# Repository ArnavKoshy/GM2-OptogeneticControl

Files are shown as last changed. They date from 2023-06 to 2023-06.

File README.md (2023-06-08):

# GM2-OptogeneticControl
A repository holding information and resources about the GM2 project about optogenetic control in bioreactors for enzyme synthesis

For information about the project, what we've done and how it relates to UN Sustainable Development Goals, see [About](About/)

For information about the testing rig used to collect light intensity data around a bioreactor, see [Testing Rig](Testing%20Rig/)

For information about our light distribution model, see [Modelling](Modelling/)

For information about the final lighting rig design to light a bioreactor, see [Lighting Rig](Lighting%20Rig/)

**For Alexandre**: A list of handover documentation we've each individually contributed to is available in [Individual handover notes](Individual%20Handover%20Notes.md)

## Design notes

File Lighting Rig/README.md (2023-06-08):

# Lighting Rig Documentation

Author: Tse En Chia

## Description
---

This folder contains all the files for the design and printing of the lighting rig.

For file description and design specifications, see [CAD Files and Design Specifications](#cad-files-and-design-specifications)

## Lighting Rig Design Information
---

In the design process of the final lighting rig, a few main requirements had to be met.

1. Adequately Light

    The lighting rig should be light enough for easy transportation and set up. Users may also choose to take measurements during the synthesis process, thus the rig should be light enough to ensure ease in removing and setting it up again.

2. Low Cost

    The premise of the project was to target users in “the poorest billion”, or specifically to be deployed in Cameroon and Kenya. The cost of our design should therefore be kept as low as possible.

3. Easily Accessible

    Our partner mentioned that in previous trials, there was difficulty in accessing and installing the LED strips within the shell of the rig. Should any maintenance be required, users would also have to access the interior of the rig.

4. Easily Modifiable

    Users who wish to adopt this method of optogenetic induction would also have varying bioreactor specifications depending on their use case. Heating jackets and water jackets may be used, and users may have different volumes of bacteria and sizes of bioreactors, all of which would affect the size of the lighting rig required. The designed rig should therefore be easily customizable for users. 

## Lighting Rig Design
---

The final design of the lighting rig is as shown in the image below. This can be viewed in the assembly file.

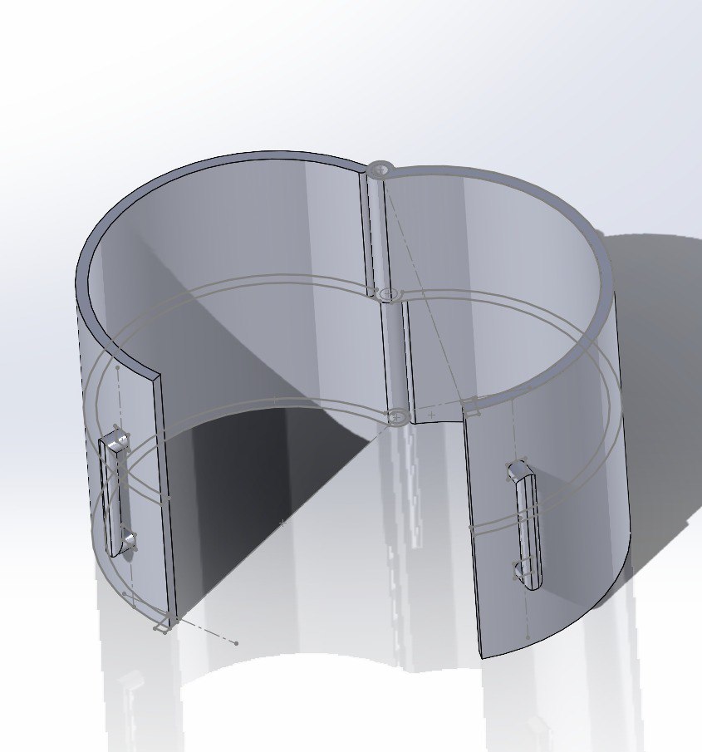
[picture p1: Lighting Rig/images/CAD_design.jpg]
CAD design


The rig uses a 6.35mm diameter rod to act as a pin for the hinge, with two halves that open to allow users to access the interior. Detailed information on the specifications can be found below in [CAD Files and Design Specifications](#cad-files-and-design-specifications).

The two halves of the rig have been designed to be secured by Velcro strips, wrapped around the handles. Users may replace this with material they deem fit to hold the halves together should a Velcro strips be unavailable (e.g. using a string to tie a knot).
  
## LED Arrangement
---

The recommended LED arrangement would be as shown in the diagram below.

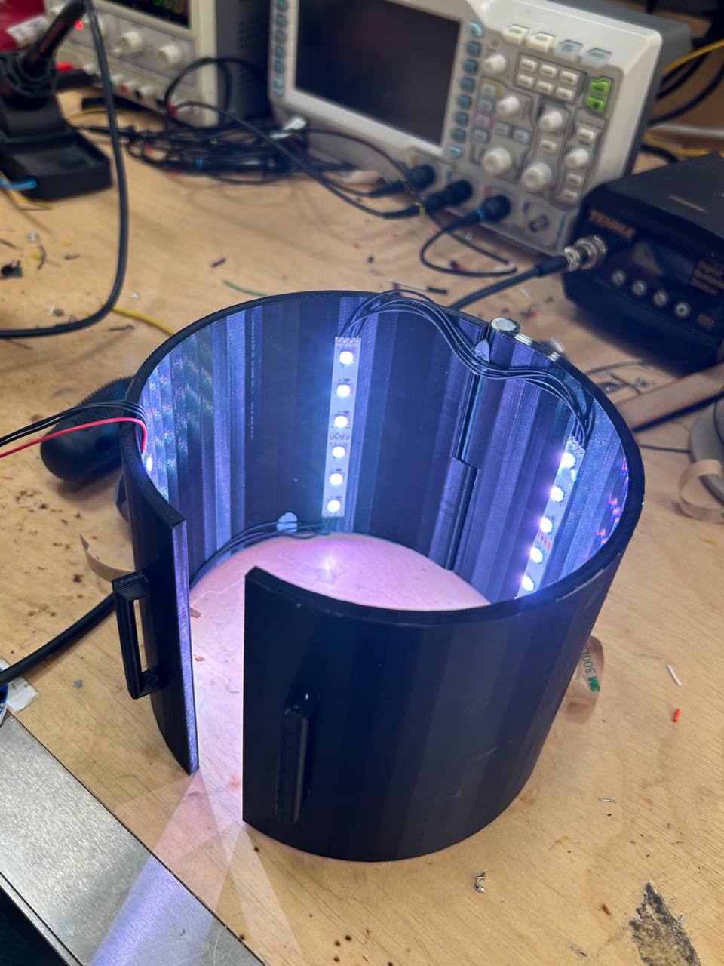
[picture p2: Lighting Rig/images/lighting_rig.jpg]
lighting rig

  
Four LED strips were installed vertically with equal spacing in the interior of the rig. The reason for this design would be because there is approximately an equal intensity of light for an arc length of about 140 degrees opposite to where the light originates from. This is supported by data collected from our tests which can be found [here](https://github.com/ArnavKoshy/GM2-OptogeneticControl/tree/main/Testing%20Rig).
  
Adding more LED strips would lead to a higher rate of bacteria synthesis but would require more electrical energy to power, which is undesirable for our target users. The recommended design saves about 80% the amount of electrical energy as compared to covering the interior with LEDs. We **do not recommend** using lesser LED strips as this would lead to some parts of the bioreactor not being illuminated.
  
It is also recommended to cover the interior of the rig with a reflective surface (e.g. aluminium foil) to maximise the intensity of light being shone into the bioreactor.

## CAD Files and Design Specifications
---

  The CAD files are as follows:

- `hinge_tube_right.SLDPRT`

  The half of the rig that contains the lower knuckle (or “hinge joint”) of the hinge. The bottom of the knuckle is sealed to prevent the rod from falling out.

- `hinge_tube_left.SLDPRT`

  The half of the rig that contains the upper knuckle of the hinge. The hole of the knuckle goes all the way through for the rod to be inserted. To further secure the rod, blutack can be used to seal the top, although not necessary.

- `prototype.SLDASM`

  Contains the assembly of the lighting rig. Can be used to view the full model.

For ease of modifying the size of the structure, both files have the following global variables. Changing the values of the variables will easily change the dimensions of the structure.
  
- `DIAMETER`

  Inner diameter of the structure. Remember to cater for the height of the LEDs to be installed, and any other equipment to be placed between the jar and the rig (e.g. water jackets). The diameter set in the design file is 142mm given a bioreactor diameter of approximately 125.5mm.

- `ROD_DIAMETER`

  Diameter of the rod used as the hinge pin. Set a buffer of 0.5mm-1mm depending on the print accuracy. The ROD_DIAMETER in the design file was set to 7mm, given that a steel rod with a diameter of 6.35mm was used.

- `HEIGHT`

  Desired height of the structure. The height in the design file was set to 130mm.

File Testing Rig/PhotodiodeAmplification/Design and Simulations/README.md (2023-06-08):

# Simulation and circuit design

This document outlines the initial design process for the amplification circuit elements, in case a ground-up redesign is considered.

## Amplifier Stage Design

###### Overview
The amplification circuit uses trans-impedance amplifiers (TIAs) to amplify the minute photodiode currents caused due to incident light. For the photodiode chosen, this current varies from $10nA$ to $50\mu A$.

The gain of the TIA is set by a single gain resistor. The output voltage is given by $I_d R_g + V_{off}$ where $I_d$ is the current through the diode, $R_g$ is the gain resistance and $V_{off}$ is the offset voltage applied to the non-inverting input. An additional capacitor is included to reduce noise.

The value of $R_g$ was chosen to allow the full range of currents through the diode to be measured. (See [Improvements](#improvements-for-redesign))

The choice to multiplex photodiodes before the amplifiers was made due to the significant cost and complexity benefits it provides. Only 3 amplifiers were needed, which amounted to a single chip, as opposed to the potential 6 ICs that would be needed without multiplexing.

###### Inclusion of Offset voltage
The amplifiers used are advertised as rail-to-rail, but actually can only drive outputs $25mV$ above $V_{ss}$ or below $V_{dd}$. 

In order to stay out of this region, a $50mV$ offset voltage was applied, so that the lowest output voltage of the TIA would always be $50mV$

###### Effect of multiplexer on resistance

When using a multiplexer before the inverting input of the amplifier, the resistance of the multiplexer was considered to confirm it had no impact on amplified reading. This was clear from a back-of-the-envelope circuit analysis, and was further verified in simulation.

## Simulation

[PhotodiodeStage.asc](PhotodiodeStage.asc) is an [LTSpice](https://www.analog.com/en/design-center/design-tools-and-calculators/ltspice-simulator.html) simulation of a single amplifier and photodiode. 

Photodiodes are not a standard part in the LTSpice library, so a phototransistor was used. This has a very similar working principle so was considered to be a usable substitute. 

The multiplexer resistance was taken into account with R3 - a $100 \Omega$ series resistance between the phototransistor and the inverting input of the amplifier.

A transient simulation has been set up for steadily increasing incident light on the phototransistor.

## Improvements for redesign

The photodiodes and amplifiers worked well in broad daylight, but were not sensitive enough for the low light intensities of bioreactor illumination. A different choice of photodiode would be beneficial, with a steeper current-light relationship. 

The gain resistance could also be changed to achieve the same effect.

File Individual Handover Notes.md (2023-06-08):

### Here's the links of handover notes that each of our group member wrote/contributed:

Arnav:
- [Modelling Handover](/Modelling/DiffuseSim/README.md)
- [Data Collection Handover](/Testing%20Rig/DataCollection/README.md)
- [Circuit Design and Simulation Notes](/Testing%20Rig/PhotodiodeAmplification/Design%20and%20Simulations/README.md)
- [Arduino Handover](Testing%20Rig/Arduino/datalogging/README.md)

Alban: 
- [Data Analysis](/Testing%20Rig/Data%20Analysis/README.md)
- [Further Testing](/Testing%20Rig/Further%20Testing/README.md)

Jasmine:  
- [Circuit Design Handover](https://github.com/ArnavKoshy/GM2-OptogeneticControl/blob/main/Testing%20Rig/PhotodiodeAmplification/Circuit%20Documentation.md)  
- [Experimental Data Analysis Handover](https://github.com/ArnavKoshy/GM2-OptogeneticControl/blob/main/Testing%20Rig/Data%20Analysis/Data%20Analysis%20Documentation.md)  

Tse En:  
- [Testing Rig Physical Design Handover](https://github.com/ArnavKoshy/GM2-OptogeneticControl/blob/main/Testing%20Rig/Physical%20Rig/README.md)
- [Lighting Rig Handover](https://github.com/ArnavKoshy/GM2-OptogeneticControl/blob/main/Lighting%20Rig/README.md)

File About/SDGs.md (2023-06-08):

# The project and Sustainable Development Goals

The project's impact can be assessed by considering how closely it aligns with the following UN [Sustainable Development Goals](https://www.globalgoals.org/goals/)

## Reduced inequalities
---
Enzymes are a crucial component when it comes to essential chemical processes such as water purification, or disease treatment and detection.
The components act as catalysts in chemical reactions, and are needed in the Global South.

The problem however, is that enzyme imports are very scarce, expensive and the delivery time is high. 
Furthermore, the local synthesis of enzymes requires reagents, which are also hard and expensive to deliver to poor countries.

Enzymes are needed in the Global South, but can't be acquired sustainably to satisfy the needs.

One solution that may be able to improve that problem is using Optogenetics.
The principle is the following: by directing light at bacteria, there is a production of enzyme. This is of course wavelength and intensity dependant, but this solution is fairly simple to implement and promising.

This allows better access to enzymes in the Global South, reducing access inequalities to products necessary for research towards other development goals.

## Resilient infrastructure - distributed production of enzymes
---
Optogenetics is conducted in a structure that is called a bioreactor. The bioreactor is container ranging in volume from 500mL to a few dozens of litres.
Once the bioreactor is acquired, and the lighting rig is setup, all there is to do is to put bacteria in the reactor and start the optogenetics process. 

Bacteria are easily accessible even in Global South countries, which enables them to have a resiliant enzyme supply chain. Moving the production of enzymes to the place of use is beneficial in improving the resilience of supply chains to disruption and shortage, as well as reducing acquisition times.

In terms of setup, the solution we came up with only uses an Arduino card, which can be run by any basic laptop, and LEDs which are easily found anywhere in the world. One step further from our project would be to design specifications that can take into account most LED specs and adapt the solution accordingly.

## Sustainable economic growth
---
Optogenetics allow countries in the Global South to not rely on enzyme or reagents import, and to produce enzymes locally. This allows independent economic growth of research sectors of these countries, without depending on foreign imports. 

Furthermore, the vast majority of the components needed to run our setup can be sourced locally.

An Arduino card, LED strips, 3D printed parts and any laptop are components that can be obtained very quickly and easily.

This makes the enzyme production local and virtually independant from any imports.

## Partnership towards the goals.
---

Enabling production of necessary enzymes in developing countries facilitates them to independently work towards other UN Sustainable Development Goals without relying on foreign supplies. 
This, coupled with the reduced acquisition time for necessary enzymes, dramatically accelerates the pace of research and progress in developing countries.

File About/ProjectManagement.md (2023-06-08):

# Project Management

## Gantt chart
To organise the project, [ClickUp](https://clickup.com/) - a project management tool - was used. This had several advantages. Tasks could be assigned to individual people. The progress of the project could be monitored centrally, and deadlines and dependencies were clear.

The Gantt chart provided a lot of value, not only to schedule tasks and monitor project progress, but also to organise dependencies and consider tasks that were blocking others.

The images below show a comparison of the initial Gantt chart plan, with the final actual chart being shown below.

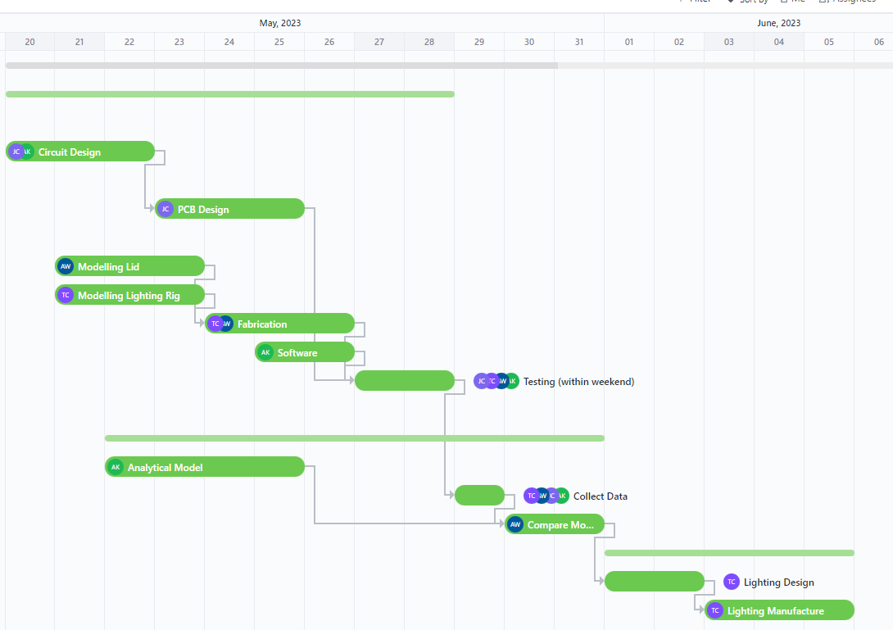
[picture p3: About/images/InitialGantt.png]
Initial chart


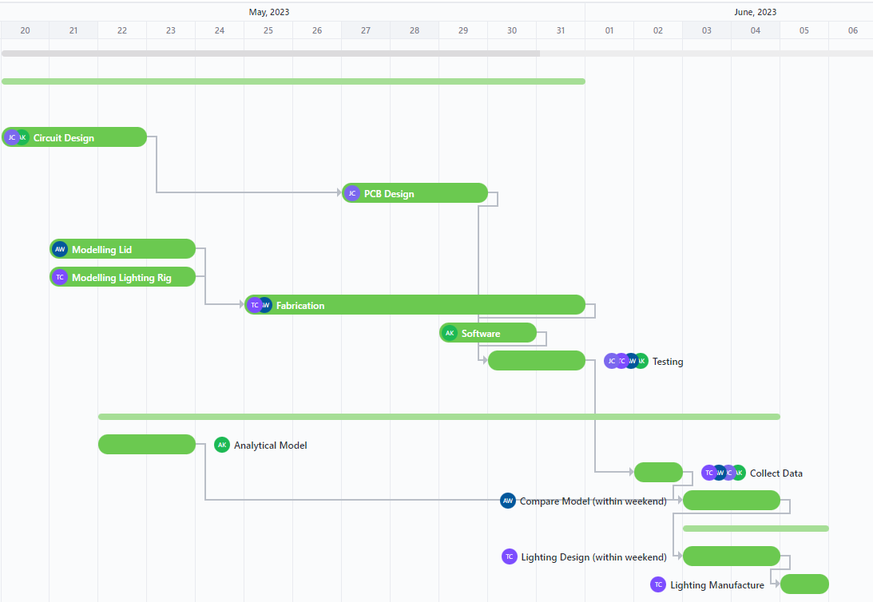
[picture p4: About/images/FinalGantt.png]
Final chart


The key differences are as follows (also see [Setbacks](#setbacks)):
- Electronics were highly delayed due to delays in component delivery
- 3D printing of parts took longer than expected due to redesigns and print issues
- Due to electronics being delayed, the final testing and prototyping was also delayed till quite late.
- This delay in testing and prototyping also delayed the collecting and analysis of data.
- This meant there was not enough data to inform the design of the final lighting design, so this was also delayed.
- The analytical model was abandoned, and a discrete computational model used instead, which took significantly less time to implement.

## Task distribution

A challenging aspect of the project was allocating tasks to the most suitable team member. This had to take into account how comfortable each team member was with each task, how much they wanted to do it and how much work they would be doing at the same time.

Verbal discussions were useful in ascertaining what each task would require and which team members would be suitable.

ClickUp was useful for to keep track of what each team member's current tasks were in a centralised system. This allowed tasks to be distributed evenly and avoided overloading any one person.

## Design reviews

A very useful part of the design process was collaborative design reviews of each other's work. These found issues with designs and potential design improvements across mechanical, electrical and software design tasks. 

Design reviews were informally scheduled at the end of each task. While these reviews were helpful, additional design reviews during each task would have prevented the occasional complete redesign which set the project back.

## Setbacks

The following are a few setbacks the team encountered, and ways that they could be avoided in future:

##### Delivery delays leading to a reduction in scope and delay in fabrication:

There was a considerable delay in delivery of multiplexers, which had to be re-ordered. This meant that the circuitry was limited to a maximum of 8 photodiodes. Data was desperately needed, so testing progressed with 8 photodiodes instead of 24. 

The delays due to external factors, but more could have been done to reduce their impact. Extra contingency time could have been planned in to allow lee-way for delivery. Component ordering could have been carried out sooner, before the circuit design was finalised but when the general concept had been decided on.

##### Redesigns leading to delays in manufacturing:

Some components had to be redesigned several times due to their strict dimensional requirements. The design-manufacturing process had an iteration time of about a day, so each design iteration caused significant delay. 

To mitigate this, one could use more careful design process from the outset to reduce the number of design iterations. If this is not feasible, reducing the time per design iteration by using quicker manufacturing methods would also work.

##### 3D printing issues leading to delays in manufacturing:

Several setbacks occurred when 3D printing, including printers running out of filament, abandoning or ruining prints halfway through printing, and a shortage of usable printers. 
Since the electronics were more delayed than the physical components of the testing rig, these issues didn't have much of an impact on the trajectory of the project. However, steps could be taken to mitigate such delays in the future.
Attempting to salvage ruined prints rather than reprinting was an approach that worked occasionally, but could still be explored further.

##### Infeasability of analytical model

Initially, the team was working towards a closed form analytical model for light distribution in a bioreactor. However, it quickly became apparent that this was not a simple task. After several failed attempts at a model, the exact design requirements were re-considered and a computational approximation was deemed suitable. This proved easier to implement and more flexible overall.

## Failure analysis of electronics

The largest failure of the project was the failure of the final stripboard circuit with 24 photodiodes. This prevented the team from gathering further data which would have proved invaluable in further assessing the model and designing the lighting rig. 

A post mortem analysis of this failure presents some things that should have been done differently to avoid such a failure in the future.

The root cause of the failure is hypothesised to be a faulty Arduino. The Arduino stopped working after placing the exposed copper traces of the stripboard circuit on a conductive surface, likely shorting some pins. The chain of reasons that led up to this single failure point can be further deconstructed: 

1. Components ordered late
2. Component delivery delays make prototyping infeasible
3. PCB deemed too risky without prototyping circuitry first
4. Circuitry prototyped on stripboard
5. Stripboard placed on conductive surface
6. Arduino dies
7. Not enough time for replacement due to delays
8. Testing cannot take place as planned.

If any one of those factors had not happened, it is unlikely the same failure would have occurred. The easiest reason above to rectify in hindsight would be to order components earlier, allowing more time for delays. 

The Arduino was also the only component for which spares were not bought, due to its higher price. Buying spares would have meant a drop in replacement would have been usable. 

Having a PCB manufactured, regardless of confidence, might have still been beneficial. The design had been completed, so nothing would have been lost by ordering one. If the PCB had worked, a stripboard would have not been necessary and the circuit would have been more robust. If the PCB had not worked, nothing would have been lost.

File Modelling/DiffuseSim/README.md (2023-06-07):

# Modelling documentation
Author: Arnav

## Description
---

This folder contains the files necessary to run a numerical discretized light simulation model. **This model is not accurate, see [Limitations](#limitations)**.

For an overview of how the model works, see [How it works](#how-it-works).

## File descriptions
`main.py` contains the primary code which carries out a simulation of a cross section of a circular bioreactor with a single point source of light.

`benchmark.py` carries out a simulation similar to that in Figure 5. of [this paper](https://www.spiedigitallibrary.org/journals/journal-of-biomedical-optics/volume-19/issue-04/045003/Monte-Carlo-simulation-of-light-transport-in-turbid-medium-with/10.1117/1.JBO.19.4.045003.full?SSO=1&tab=ArticleLinkFigureTable) in order to compare results.

`main3D.py` offers an example of how the simulation could be extended to 3 dimensions if vertical light propagation was also of interest. 

## Instructions to run
---

### Requirements:
    - Python 3.10 or later
    - Python pip
    
### Instructions for setup

Install necessary modules with `pip install -r requirements.txt`

Then run `python main.py`

## How it works
---

The model works by splitting the area of the bioreactor into a set of randomly positioned discrete points. 
These points each act as pockets of fluid, both scattering and attenuating the light that passes through them.

### Attenuation
The attenuation of light passing through the medium is modelled using the [Beer-Lambert law](https://en.wikipedia.org/wiki/Beer%E2%80%93Lambert_law): $I = I_0 e^{-\mu l}$ where $l$ is the distance travelled by a light ray, and $\mu$ is the absorption coefficient of the fluid. This attenuation coefficient can be modified to take into account different attenuations of different wavelengths. **This model of attenuation is wrong, see [Limitations - attenuation](#limitations-of-attenuation)**.

The rays of light created by the source (shown in orange in the figure below) are assumed to pass through turbid fluid on the way to each point, attenuating with the Beer-Lambert Law.

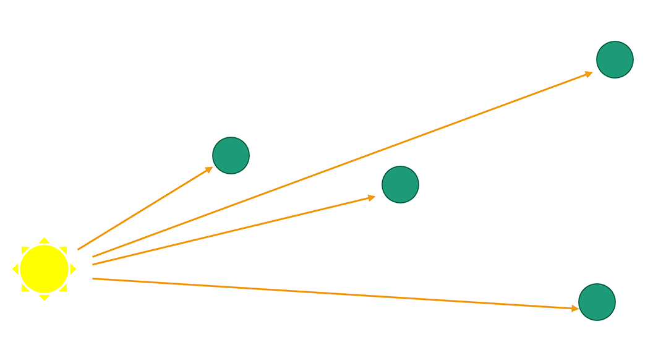
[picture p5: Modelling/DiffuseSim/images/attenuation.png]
Light attenuation


The Beer-Lambert law only considers light travelling in a straight line, and does not consider the scattering of light due to the fluid, and this has to be taken into account separately.

### Scattering
Scattering is considered by a phenomenon known as [Lambertian cosine law](https://www.sciencedirect.com/science/article/pii/B9780123860224000066), which describes the behaviour of light as it passes through a diffuse medium. The intensity of light varies with the cosine of the angle to the incident ray, as shown in the figure below. This is not the only scattering model, as discussed in [Limitations - scattering](#limitations-of-scattering)

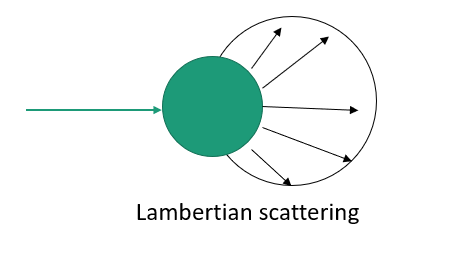
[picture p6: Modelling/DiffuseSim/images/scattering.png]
scattering


Scattered light from each point is also attenuated as it progresses to every other point in the model, as shown by the green arrows. The final intensity is the sum of the direct light from the point source and scattered light from every other point.

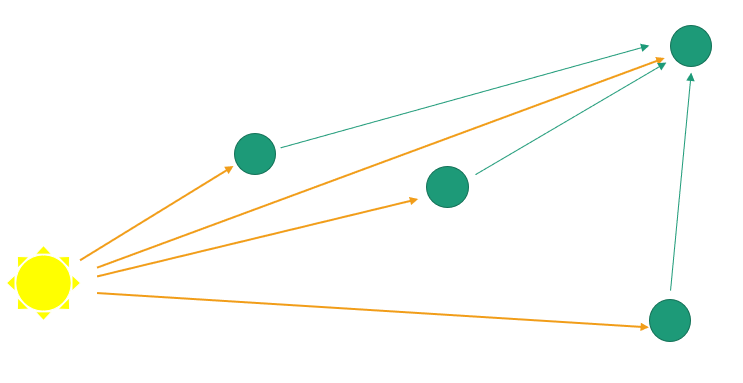
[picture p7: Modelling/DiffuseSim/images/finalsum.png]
final light paths


## Limitations

### Magnitudes and units
###### The issue:
The model does not consider exact magnitudes and units of light, and should at this stage be only used as an approximation for spatial light distribution within a turbid vessel.

###### How to fix:
Addition of units might involve specifying the power of the light source and then calculating incident power at each discrete point, taking into account attenuation.

### Limitations of Attenuation

###### The issue:
The attenuation equation used in the model is incorrect. It does not take into account the inverse square law attenuation of the light from the point light source. 

This means that the radial distribution of the light from the point source is incorrect. However this should not have much effect on the overall shape of the graph of circumferential light intensity, but rather drastically decrease the magnitude.

###### How to fix:
Fixing this would firstly involve implementing the inverse square law attenuation in the attenuation function (`LightModel.py line 20`) for both direct illumination from the light source and scattered light.

To prevent numerical instabilities due to very closely spaced points, it could be beneficial to move away from randomly positioned points and towards a more uniform distribution such as a grid or Poisson disc sampling.

### Limitations of scattering
###### The issue:
The scattering model used assumes perfect diffusion of incident light with the Lambert cosine law. In reality, the distribution of scattered light may look more like [Mie scattering](https://en.wikipedia.org/wiki/Mie_scattering) or similar. The amount of scattered light is assumed to be proportional to the characteristic dimension of each pocket of fluid, which may not be valid.

###### How to fix:
The scattering function can be changed to better reflect a more realistic scattering distribution. An angle variable has been included to be passed to a custom function in `LightModel.py line 75`

### Limitations of light source
###### The issue:
The light source is modelled as having a light intensity that varies with the cosine of the angle from its forward direction. This is a good approximation of the LEDs used for the testing rig, but may not be representative of your lighting.

###### How to fix:
`LightModel.py line 40` exposes an angle variable that can be passed into a custom function that returns a light distribution factor describing the spread of light from a light source.

### Computational speed
###### The issue:
The software is written in Python and not well-optimised, so the simulation is quite slow. Additionally, there are no approximations used to speed up the computation, so the simulation is $O(n^2)$ complexity, which makes it very slow for large numbers of points.

###### How to fix:
One solution would be to port the code to a different more performant language, such as C++. Otherwise, speed ups could be implemented in Python by using faster algorithms for the spatial computation, potentially by ignoring far away points or considering them in groups using something like [Barnes-Hut](https://jheer.github.io/barnes-hut/) adapted for light intensity rather than forces.

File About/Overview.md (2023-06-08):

# Project Overview

## Problem Overview

In many developing countries, the gaps in terms of research and equipment is significant. An example of this is the limited access to reagents for enzyme synthesis. This limits the efficacy of research and development in developing countries. One proposed solution is to use optogenetics to induce the production of enzymes without needing reagents. This allows researchers with limited access to inducing agents to synthesis enzymes by illuminating bacteria. See [this paper](https://pubmed.ncbi.nlm.nih.gov/33255280/) for more information **In this project, our group cooperates with Jenny Molloy to improve the optogenetic device.**

 

## Technical Summary

  

Multiple optogenetics designs has already been built previously, and their literatures helped us greatly to start up the project. However, one main problem with these designs is a lack of experimental data on light intensity and quantitative analysis to inform the design of an effective illumination system for a bioreactor with optically sensitive bacteria.
To solve this problem, we built a testing rig that measures the light intensity circumferentially to collect experimental data. We also came up with a numerical model, which is implemented in python and effectively simulate the light transmission behaviour through any cylindrical container. 
After data collection, we put the experimental data and analytic solution together and fit the parameters in the theoretical model, and evaluated its behaviour.



Above is the prototype of our testing rig and lighting rig.  

## Results and Further improvements


The testing rig and model has satisfactory behaviour considering the time scale and resources we're given, and they demonstrated the feasibility of our model. However, there are several possible improvements listed above.  
What's more, on the biology side of this project, it would be idea to have further data analysis and modelling relating the light intensity to the actual bacteria growth rate, which we cannot easily implement. Combining this to our current outcome will achieve allow more advanced solutions such as using PID control to control bacterial activity.

### Compatibility
We're aware that in developing countries the availability of components can be quite limited. Also, depending on the type of bacteria there may be different setups. For example, the wavelength of LED may be changed in different scenario. Our electrical design documentation had taken this into account and gave suggestions for substituting components. However, the modelling also require modification in that case, which would be feasible by changing model parameters.

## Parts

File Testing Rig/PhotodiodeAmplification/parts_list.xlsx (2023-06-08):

Part Number | Quantity | Description
MCP6004-E/P | 3 | MICROCHIP Operational Amplifier, Quad, 4 Amplifier, 1 MHz, 0.6 V/Âµs, 1.8V to 6V, DIP, 14 Pins
CD74HCT4051E | 5 | TEXAS INSTRUMENTS Analog Multiplexer / Demultiplexer, 8:1, 1 Circuit, 90 ohm, 16 ÂµA, 4.5V to 5.5V, DIP-16
ABX00028 | 1 | ARDUINO Single Board Computer, Arduino Nano Every, ATMega4809, 48KB Flash, 6KB SRAM, 256byte EEPROM
51067-0400 | 3 | MOLEX Connector Housing, Mighty-SPOX 51067, Receptacle, 4 Ways, 3.5 mm
2227MC-14-03-10-F1 | 5 | MULTICOMP PRO IC & Component Socket, 14 Contacts, DIP Socket, 2.54 mm, 2227MC, 7.62 mm, Beryllium Copper
MC34631 | 5 | MULTICOMP PRO Pin Header, Wire-to-Board, 2.54 mm, 1 Rows, 3 Contacts, Through Hole Straight, MC34
MC34483 | 5 | MULTICOMP PRO Connector Housing, MC34, Receptacle, 3 Ways, 2.54 mm, 2218T Crimp Contacts
22-29-2041 | 4 | MOLEX Pin Header, Signal, Wire-to-Board, 2.54 mm, 1 Rows, 4 Contacts, Through Hole Straight, KK 254 6410
22-01-2047 | 4 | MOLEX Connector Housing, KK 254 2695, Receptacle, 4 Ways, 2.54 mm
SFH 203 P | 30 | AMS OSRAM GROUP Photo Diode, 75Â° Half Sensitivity, 1nA Dark Current, 850nm, T-1 3/4 (5mm)-2 Pins
IRLZ24NPBF | 6 | INFINEON Power MOSFET, N Channel, 55 V, 18 A, 0.06 ohm, TO-220AB, Through Hole
2218T | 20 | MULTICOMP PRO Contact, 2218, Pin, Crimp, 22 AWG, Tin Plated Contacts
L7805ABV | 3 | STMICROELECTRONICS Fixed Linear Voltage Regulator, 7805, 3-Terminal, Positive, 10V To 35V In, 5V And 1.5A Out, TO-220-3
SR211C104KAR | 8 | KYOCERA AVX Multilayer Ceramic Capacitor, 0.1 ÂµF, 100 V, Â± 10%, Radial Leaded, X7R, 5.08 mm
MC0805B334K500A5.08MM | 3 | MULTICOMP Multilayer Ceramic Capacitor, 0.33 ÂµF, 50 V, Â± 10%, PC Pin, X7R, 5.08 mm
K220J10C0GF5UH5 | 5 | VISHAY Multilayer Ceramic Capacitor, 22 pF, 50 V, Â± 5%, Radial Leaded, C0G / NP0, 5 mm
MCF 0.5W 10K | 15 | MULTICOMP PRO Through Hole Resistor, 10 kohm, MCF, 500 mW, Â± 5%, Axial Leaded, 350 V
MF12 1M | 5 | MULTICOMP PRO Through Hole Resistor, 1 Mohm, MF12, 125 mW, Â± 1%, Axial Leaded, 200 V
MF25 100K | 10 | MULTICOMP PRO Through Hole Resistor, 100 kohm, MF25, 250 mW, Â± 1%, Axial Leaded, 250 V
PPW01010 | 1 | PRO POWER DC Power Connector, Receptacle, 2.1 mm, PCB Mount, Solder
694108301002 | 1 | WURTH ELEKTRONIK DC Power Connector, Jack, 5 A, 2.5 mm, PCB Mount, Solder
90160-0126 | 1 | MOLEX Connector Housing, C-Grid III 90160, Receptacle, 26 Ways, 2.54 mm, 90119 Crimp Terminal
90130-1126 | 1 | MOLEX Pin Header, Signal, 2.54 mm, 2 Rows, 26 Contacts, Through Hole Straight, C-Grid III 90130 Series
90119-0109 | 35 | MOLEX Contact, C-Grid III&trade;, C-Grid III 90119, Socket, Crimp, 22 AWG, Tin Plated Contacts

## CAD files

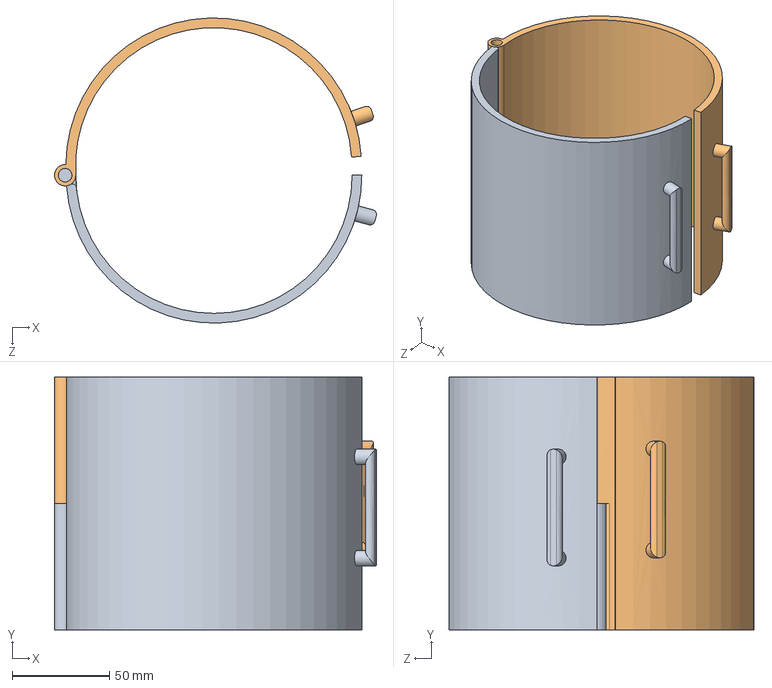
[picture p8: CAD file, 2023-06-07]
Lighting Rig/prototype.SLDASM
165.5 x 130.0 x 156.8 mm
1hinge tube right
1hinge tube left

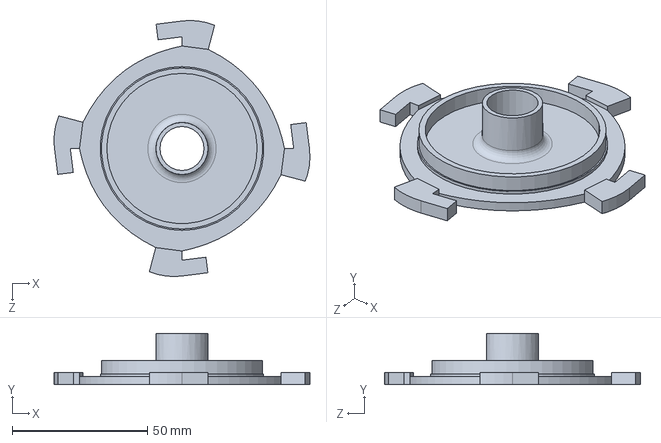
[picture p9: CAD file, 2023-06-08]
Testing Rig/Further Testing/internal_testing_lid.SLDPRT
94.8 x 19.0 x 94.8 mm

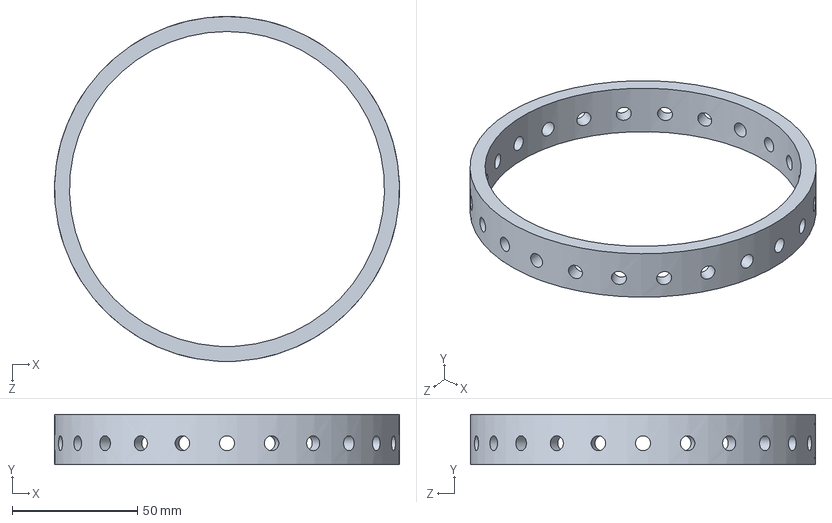
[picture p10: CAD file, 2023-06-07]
Testing Rig/Physical Rig/sensor_ring.SLDPRT
138.0 x 20.0 x 138.0 mm

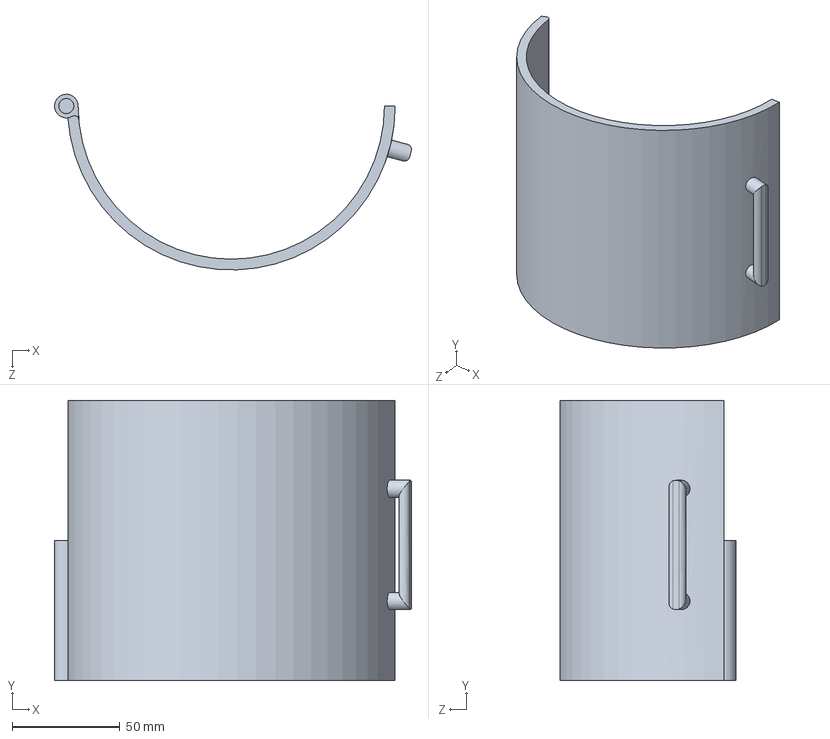
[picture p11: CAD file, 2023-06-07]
Lighting Rig/hinge_tube_right.SLDPRT
165.5 x 130.0 x 81.4 mm

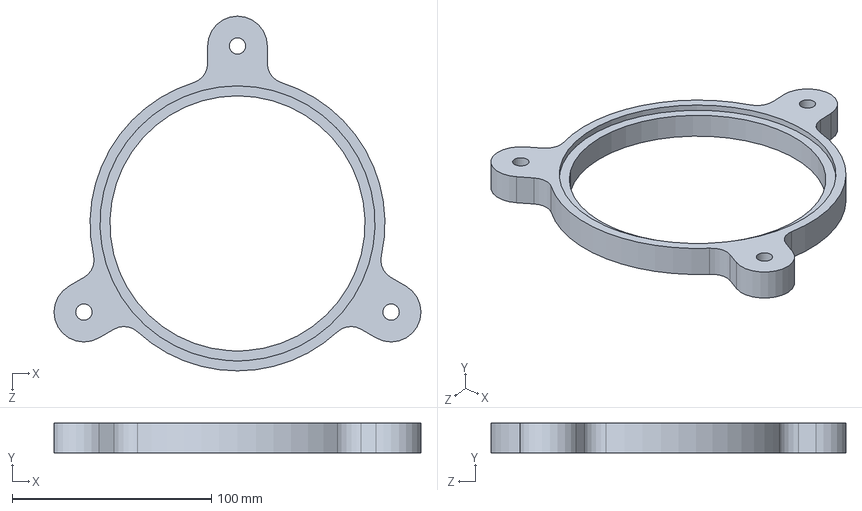
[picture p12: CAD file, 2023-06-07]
Testing Rig/Physical Rig/sensor_collar.SLDPRT
184.2 x 15.0 x 178.0 mm

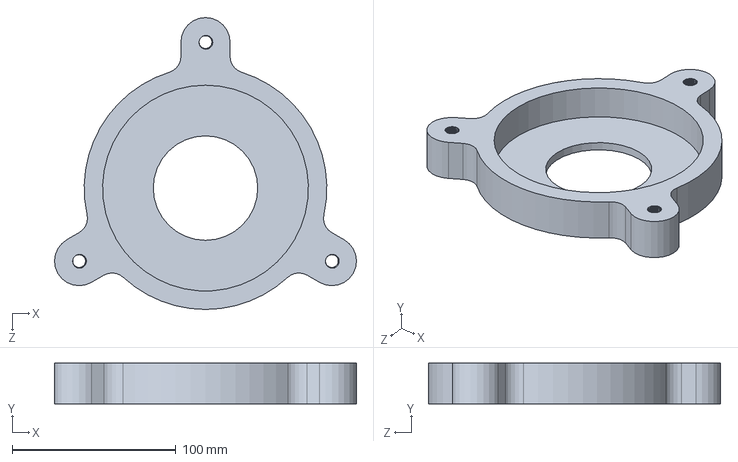
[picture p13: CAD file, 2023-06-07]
Testing Rig/Physical Rig/base.SLDPRT
184.2 x 25.0 x 178.0 mm

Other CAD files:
Lighting Rig/hinge_tube_left.SLDPRT
Testing Rig/Physical Rig/base.STL
Testing Rig/Physical Rig/sensor_collar.STL
Testing Rig/Physical Rig/sensor_ring.STL

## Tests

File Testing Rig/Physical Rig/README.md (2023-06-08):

# Physical Rig Documentation
---
Author: Tse En Chia

## Description
---
This folder contains all the files for the design and printing of the testing rig.

For file description and design specifications, see [CAD Files and Design Specifications](#cad-files-and-design-specifications)

## Testing Rig Design Infomation
---

In the design process of the physical testing rig, a few main requirements had to be met.

1.	Able to measure light distribution circumferentially around the bioreactor
2.	Adjustable height

Research done by our partner, Dr. Jenny Molloy, yielded [Kitchener et al. (2019)]( https://www.hardware-x.com/article/S2468-0672(18)30076-2/fulltext) who developed a sensor ring around a cylinder for turbidity measurement. By taking their model as reference, we then designed a testing rig suitable for our measurements.

## Testing Rig Design
---

The final design of the testing rig can be shown in the diagram below.

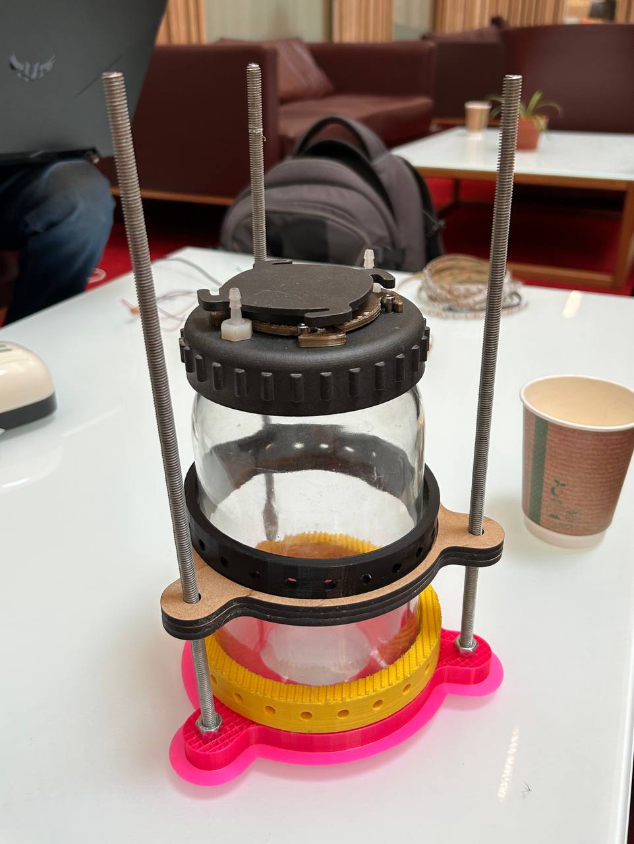
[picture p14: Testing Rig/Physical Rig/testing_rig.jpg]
Testing Rig


## CAD Files and Design Specifications
---

Using a bioreactor jar of diameter 125.5mm, the CAD files are as follows:

-	`base.SLDPRT`

  The base of the testing rig. It comes to a height of 25mm and has an internal diameter of 125.5mm. Do set a diameter slightly smaller or exactly the size of the bioreactor and file the interior to get the jar to fit perfectly. The three threaded holes are for M8 rods.
  
-	`sensor_ring.SLDPRT`

  The ring where sensors are fixed in place for measurement. This should lie on top of the sensor collar. We worked with sensors with a diameter of 5.8mm, and the sensor holes were set to 6mm. The diameter of the sensor ring was set to 126mm.

-	`sensor_collar.SLDPRT`

  The piece which controls the height of the sensors, by resting on nuts screwed into the threaded rod. The sensor ring should fit on top of this part. The diameter of the sensor collar need not be too close to the bioreactor, and has been set to 128mm. The diameter of the holes which the threaded rod passes through has been set to 8.2mm.
  
## References
---
  
Kitchener, Ben GB, et al. "A low-cost bench-top research device for turbidity measurement by radially distributed illumination intensity sensing at multiple wavelengths." HardwareX 5 (2019): e00052.
https://www.hardware-x.com/article/S2468-0672(18)30076-2/fulltext

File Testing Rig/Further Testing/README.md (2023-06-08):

# Additional testing Rig Documentation
---
Author: Alban Wales

## Description
---
This folder contains the files which will allow for more extensive testing of light intensity within the bioreactor, as our measurements were only made outside of the bioreactor, which has issues with internal reflection for instance.

In order to test internally the intensity of the light without contaminating the bacterial environment, we designed a lid that enabled us to insert a test tube with a light sensor in it, as Jenny advised this was the most effective way to conduct measurements inside the jar. Indeed, test tube are transparent and their reflective/refraction are very similar to the air's. Furthermore, they are very easy to source in lab environment. 

This lid clips on a pre-existing jar that Jenny and her team use in their experiments. 

The constraints design-wise are:
  - It has to fit on the lid base
  - A test tube has to be able to fit in the middle of it.
 
With these constraints in mind, we started to design the testing lid.

## Testing rig design
---
After a couple of unsuccessful iterations due to 3D-printing issues (gcode file issues) and wrong dimensions, we printed the following lid.





## Cad file and design specifications
---
The lid is a lid that clips on top of a pre-existing lid.

-	`internal_testing_lid.SLDPRT`

It has a hole of 8.1mm radius in its, to accomodate for a test tube when measuring light in the center of the jar. We chose to have 2mm of extra room for the test tube (16mm diameter) as 3D print can sometimes not be as accurate as expected, and to also account for the tolerance on the test tube diameter.

It features a 19 mm tube in order to guide the test tube down, and the lid is 4mm thick.

There are four clicking-on extensions, which click on into place on 4 pre-installed screws on the lid base.

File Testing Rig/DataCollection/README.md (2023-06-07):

# Data collection documentation
Author: Arnav

## Description
---

This folder contains the files necessary to collect and store data from the Arduino when running light intensity measurements.

The `main.py` file does the following:

    - Establishes a connection with the Arduino over Serial.
    - Creates a new file in which to store data of a name of your choosing.
    - Requests the Arduino for data on command.
    - Stores the received data with an associated label.

## Instructions to run
---

### Requirements:
    - Python 3.10 or later
    - Python pip
    
### Running

Install necessary modules with `pip install -r requirements.txt`

Edit `main.py lines 5-6` with the serial port and baud rate (if you've changed it) of your Arduino (To find your serial port, try [this link](https://uk.mathworks.com/help/supportpkg/arduinoio/ug/find-arduino-port-on-windows-mac-and-linux.html)).

Then run `python main.py`

Enter a file name to store data
When prompted, enter a data label for the data point being collected. The python file will request data from the Arduino, wait until it responds (or times out) and then store that data under the label specified.

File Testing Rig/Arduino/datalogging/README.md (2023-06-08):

# Arduino Code

The Arduino code is designed to collect and stream data to a laptop running the corresponding python file (See [Data Collection](Testing%20Rig/DataCollection))

The principal of operation is polling sensors with digital inputs. The sensors are selected by selecting corresponding connection on the analog multiplexer (See [Circuitry](Testing%20Rig/PhotodiodeAmplification))

The code is quite simple, and is documented internally. To run it, [Arduino IDE](https://www.arduino.cc/en/software) is required. Connect the Arduino, open code and select upload. Interfacing with the Arduino is done through Python.

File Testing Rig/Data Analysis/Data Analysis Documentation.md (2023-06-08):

# Guide to Experimental Data Analysis
Author: Jasmine

This is a brief guide that will explain the process and testing result of data analysis. It is based on the circuit design and datalogging program that is explained detailedly in the other files in Testing Rig folder.  
After data logging, you should have .csv files loading all the data you have. Here are the steps needed to calibrate the raw data to something we can use directly to build empirical formulars of the model, or for other purpurses:  

1. Zero Reading Calibration
2. Position Calibration
3. Wavelength  Sensitivity Calibration

### Zero Reading Calibration
The data you have already logged should each include a set of reading with no light source. Subtracting the raw data with this set helps remove background noises, which are inevitable in most of the cases.

### Position Calibration
For simplicity in ensembling, the apparatus we used in the testing have photodiodes randomly fitted in the testing rig, therefore before the test we covered the sensors one by one to figure out the corresponding positioning. This data is then used to remap the sensors in correct order aroung the circumference. This may not be the case in real application, as you'd probably like to label and fix photodiodes' position for simplicity. However if there's a need to do so, remap can be done as it was shown in the python code.  
The next step is to map sensor positions to angular position. As we have 24 photodiodes, after converting to angular position, we can get 24 samples with 15 degree interval.   

### Wavelength Sensitivity Calibration
The photodiodes normally have a relative sensitivity curve showing its different sensitivity corresponding to different wavelength. For SFH 203 P, which we used in our design, the sensitivity curve is shown below. 

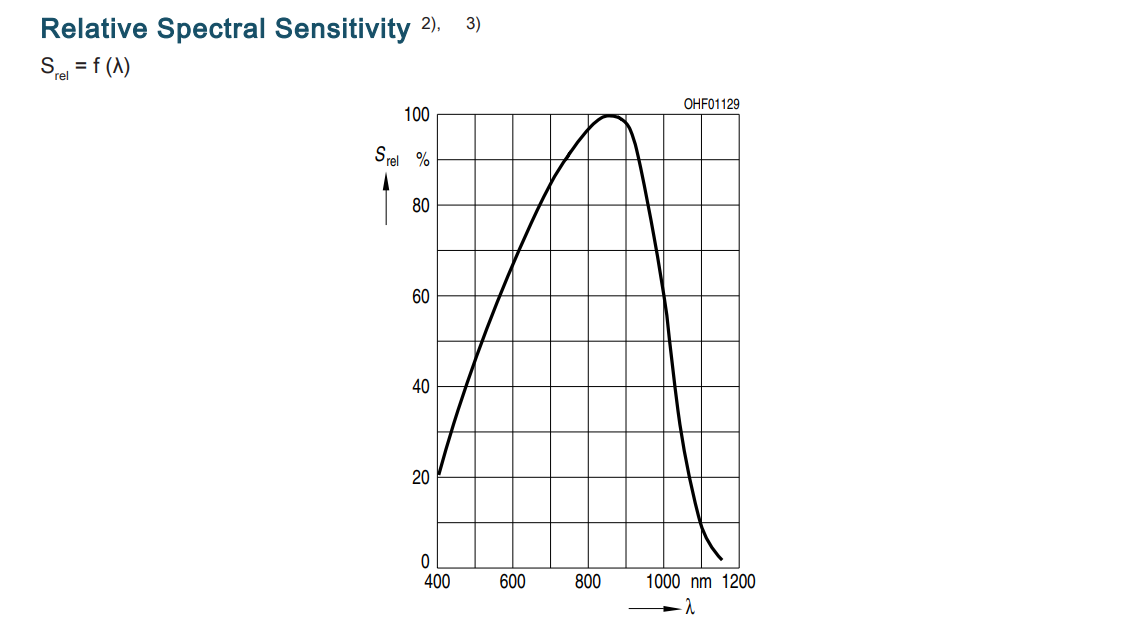
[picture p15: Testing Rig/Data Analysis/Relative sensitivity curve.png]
   

 If another other types of photodiode is used, check the datasheet for its own sensitivity curve. It's also recommonded to **check the datasheet of the LED light source used for accurate wavelength**. The code we used simply divide the corresponding datasets with red, blue and green light by their sensitivity to calibrate their light intensity reading.

## Sample results

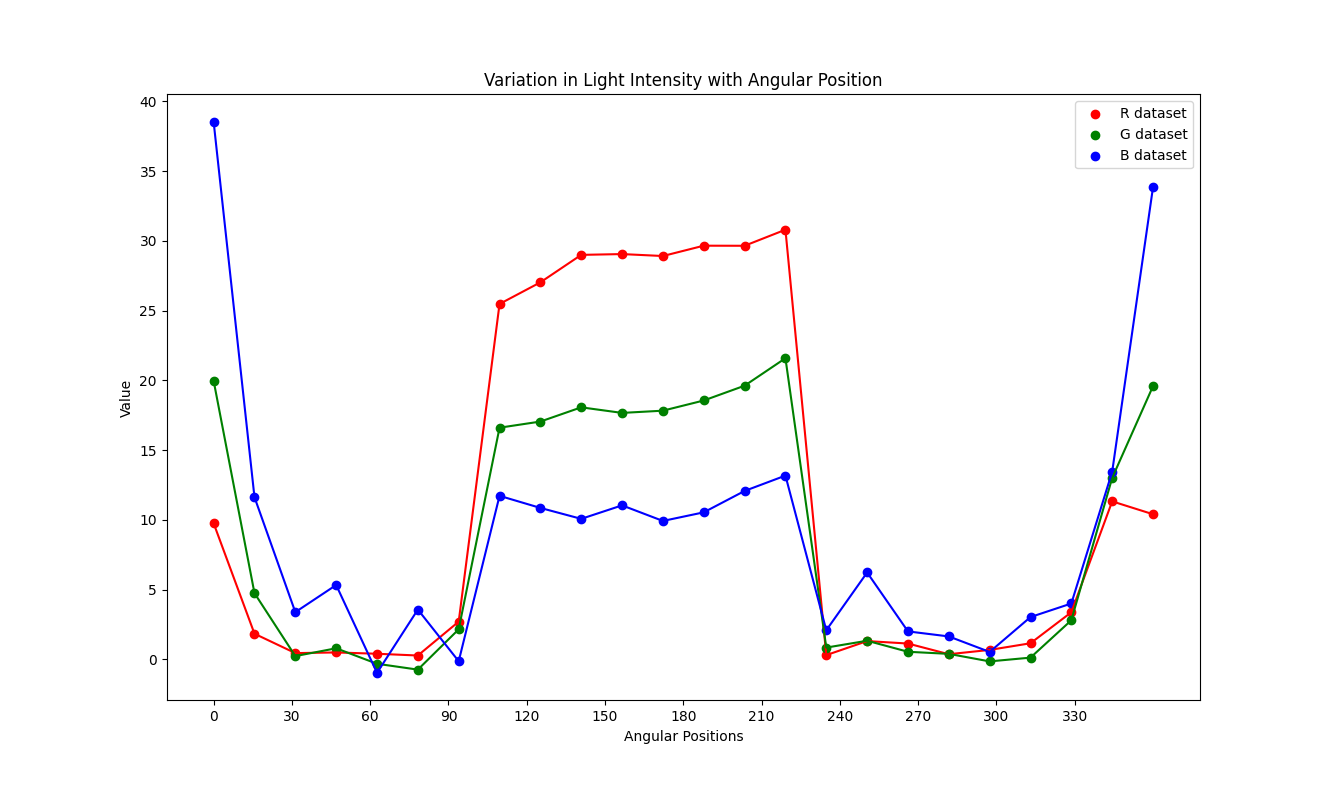
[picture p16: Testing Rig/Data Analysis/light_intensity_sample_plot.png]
    

This is a sample result that we collected with 8 photodiodes rotated twice to get all the readings in the circumference. 
The result shows that red light has the highest intensity among the three colours, and blue light has lowest intensity. This is due to the fact that the we used yellow solution in testing, which mainly absorbs blue light. After getting this curve, we can compare it with the numerical model. Refer to [Alban's writing for this in detail.](https://github.com/ArnavKoshy/GM2-OptogeneticControl/blob/main/Testing%20Rig/Data%20Analysis/README.md)

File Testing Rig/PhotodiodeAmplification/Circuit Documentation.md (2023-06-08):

# Circuit Design Documentation
Author: Jasmine  

This circuit documentation explains the design and implementation details of the circuit for photodiode amplification and data collection.
This circuit is designed in order to read signals from photodiodes. We use multiplexers to select signals, and transimpedance amplifiers to convert current signals to voltage signals.  
##### For purchasing the components, reference to the parts list in the repository: [Parts List For Referrence](https://github.com/ArnavKoshy/GM2-OptogeneticControl/blob/main/Testing%20Rig/PhotodiodeAmplification/parts_list.xlsx)  

## Table of Components
The circuits included in the circuit design in hiecharchy order:
1. Arduino Nano
2. Transimpedance Amplifiers Circuits x 3
3. 8-1 Multiplexer x 3
4. Photodiodes x 24

## Ensemble Notice
### Stripboard

For stripboard design, refer to the schematic. Here is a picture of the prototype we made: [Stripboard Prototype](git01.jpg). After building the circuit, check if there's any short circuit to avoid damaging any component. Protect the weak connections using tape or glue gun.

#### PCB design
For PCB design, refer to the kiCAD project -- PCB Editor, which should be self-explanatory.  

  

### Troubleshooting
Check the following aspects when the circuit don't work properly:
1. Powering: Is the power enough to drive the circuit
2. Short Circuits: Are there any bare wires in contact? Are the components soldered properly? 
3. Arduino: Is the Arduino functioning well without connects?

## Compatibility Notice:
If the listed cannot be purchased, here are some suggestions for replacements:
Arduino board: 
1. Arduino Uno
2. Arduino Pro Mini
3. ESP8266 NodeMCU  

Photodiodes: 
1. BPW34
2. TEMT6000
3. TSL2561  

Multiplexers:
1. 74HC4051
2. 74HC4067  

If any components are altered, remember to change the footprints in kiCAD, however due to the poor compatibility of PCB, we recommand using stripboard to reproduce the design if you'd like to change any components, otherwising there may be mismatch when soldering.

## Our testing and results

We've done a breadboard and a stripboard prototype. The breadboard testing functioned properly, but it seems it needs mounting to maintain the stability of positions of photodiodes, which will increase the accuracy and reliability of reading. The stripboard passed the testing, but before data collection the arduino board malfunctioned and cannot function correctly.



## Future Enhancements

After testing, we find out the amplification factor for the circuit can be increased further to achieve better signal-to-noise ratio. It might be helpful to use a gain resistor of larger value. The capacitor value should be adjusted as well to maintain same level of filtering.  
For powering circuits with larger power than our prototype, we may need voltage regulation to maintain the voltage supply.

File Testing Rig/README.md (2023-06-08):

The testing rig is designed to collect light intensity data around the circumference of a bioreactor. 

For documentation about each constituent part of the rig, see individual folders.

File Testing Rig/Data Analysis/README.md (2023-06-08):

# Data analysis and comparison to the model
---
Author: Alban Wales

## Variable parameters in the model
---

In the model we developed, we had two major parameters we could play with to alter the model simulation results.
1. The turbidity of the solution. Using Beer-Lambert's law, we could play with the turbidity factor to increase or decrease the attenuation of light. Attenuation is an inverted exponential of the distance to the light source multiplied by the turbidity index mu
2. The light source itself, whether it is a point source or a expanded light source.

## Comparison between the model and the experimental results
---
As shown in :
- `light_intensity_sample_plot.png`

We obtained a uniform light distribution on the circumference for all the points that were at an angle between 90 degrees and 270 degrees. On the other hand, all the other points received close to not light at all.

When running our model with a standard value of mu=0.15, we obtained the following light distribution around the circumference of the jar.

mu0 15

As the turbidity doesn't seem to be high enough, we kept increasing the turbidity, with mu=0.25 and mu=1.

mu0 25
mu=1

---

As we can see, we are starting have a curve that is flattened in the middle, which is what we want to able to model.

## Finding the right turbidity value
---
After a bit of playing around with the model, we came to the conclusion that the best mu value we could find was mu=1.38 .
mu1 38

However, we still have differences with our experimental as we don't experience as massive a drop in light intensity as in our experiments.

exp

## Limits of our experimental data
---

It is important for us to not only be critical of our theoretical model, which is a simplified version of the phenonemon, but also of our experimental data.
Indeed, such a drop in light intensity when going past a certain angle doesn't appear very physically intuitive.

We came up with two reasons that can explain this observation:
1. Our sensors have a deadzone, which prevents them from receiving light at certain angles, in our case when the angle to light source is less than 90 degrees.
deadzone

2. We have total internal reflection: in very low angles of approach, this phenomenon is very common. Light is reflected against the inner circumference of the bioreactor, and is therefore not transmitted outside to the sensors.
internal
Total internal reflection can be calculated and predicted using the Descartes-Snell law.
descartes

---
## Conclusion
---
We have been able to get our model to match somewhat closely our data by increasing the turbidity index of the media in the bioreactor.
However, it would be very interesting to further study the reasons explaining the differences between the model and the results.

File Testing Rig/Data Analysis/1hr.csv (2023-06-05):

key | value1 | value2 | value3 | value4 | value5 | value6 | value7 | value8
y0r0nolight | 38.93 | 36.49 | 8.08 | 17.79 | 2.52 | 14.03 | 38.09 | 36.10
y0r0b | 38.72 | 36.46 | 16.40 | 18.52 | 9.83 | 15.18 | 38.86 | 38.61
y0r0r | 40.50 | 47.14 | 46.53 | 19.54 | 43.53 | 15.97 | 39.16 | 43.33
y0r0g | 38.61 | 38.64 | 28.04 | 18.02 | 22.10 | 14.82 | 37.35 | 40.84
y0r1nolight | 35.23 | 8.80 | 9.89 | 16.82 | 3.22 | 14.32 | 30.00 | 36.52
y0r1b | 36.32 | 13.64 | 12.13 | 17.41 | 3.97 | 14.51 | 31.44 | 37.24
y0r1r | 38.10 | 37.06 | 13.15 | 17.73 | 3.97 | 16.00 | 38.42 | 39.34
y0r1g | 35.35 | 21.80 | 11.22 | 17.21 | 4.06 | 14.17 | 32.80 | 37.06
y0r2nolight | 29.37 | 10.50 | 9.71 | 11.87 | 7.68 | 11.57 | 22.61 | 34.16
y0r2b | 35.69 | 18.40 | 16.22 | 18.49 | 14.71 | 17.52 | 29.85 | 40.20
y0r2r | 76.21 | 59.15 | 52.40 | 57.76 | 47.92 | 57.24 | 69.44 | 79.96
y0r2g | 47.92 | 32.08 | 26.75 | 29.53 | 24.28 | 29.39 | 42.22 | 52.22
y1r2nolight | 26.02 | 10.66 | 10.26 | 12.09 | 9.36 | 11.13 | 17.62 | 33.93
y1r2b | 32.18 | 18.30 | 16.18 | 18.15 | 14.23 | 15.29 | 24.14 | 40.16
y1r2r | 67.55 | 51.84 | 46.11 | 52.26 | 41.24 | 51.28 | 60.66 | 72.20
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

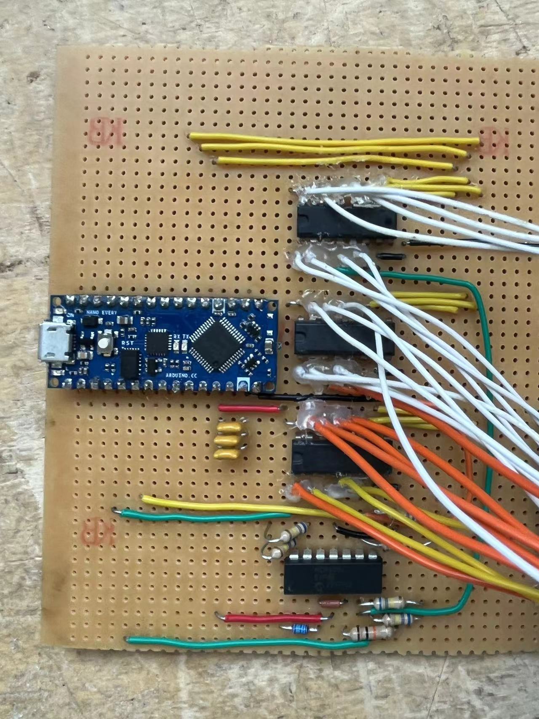
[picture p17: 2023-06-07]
Testing Rig/PhotodiodeAmplification/git01.jpg

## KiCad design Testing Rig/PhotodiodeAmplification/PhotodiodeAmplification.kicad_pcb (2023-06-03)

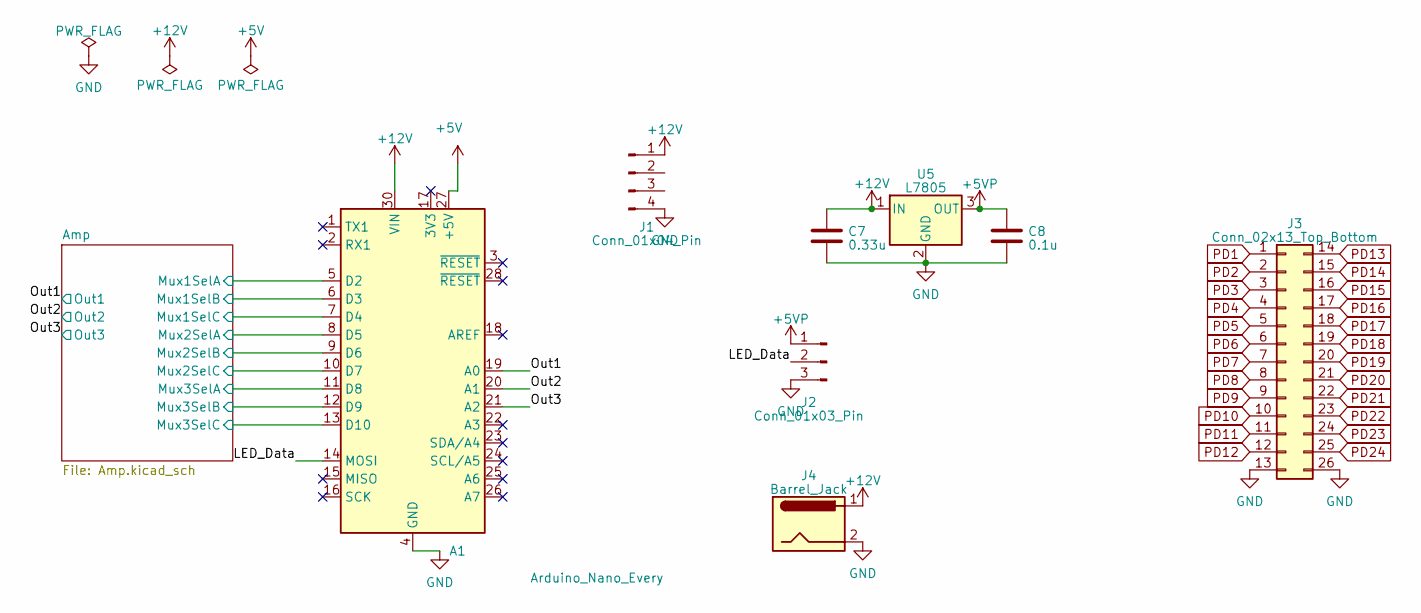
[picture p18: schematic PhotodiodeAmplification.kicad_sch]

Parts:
A1: Arduino_Nano_Every; Arduino_Nano
C7: 0.33u; C_Disc_D5.1mm_W3.2mm_P5.00mm
C8: 0.1u; C_Disc_D5.1mm_W3.2mm_P5.00mm
J1: Conn_01x04_Pin; PinHeader_1x04_P2.54mm_Vertical
J2: Conn_01x03_Pin; PinHeader_1x03_P2.54mm_Vertical
J3: Conn_02x13_Top_Bottom; PinHeader_2x13_P2.54mm_Vertical
J4: Barrel_Jack
U5: L7805; TO-220-3_Horizontal_TabDown

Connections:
+5V: A1.27 (+5V); also elsewhere on the board
+5VP: C8.1, J2.1, U5.3 (OUT)
+12V: A1.30 (VIN), C7.1, J1.1, J4.1, U5.1 (IN)
/Amp/Mux1SelA: A1.5 (D2); also elsewhere on the board
/Amp/Mux1SelB: A1.6 (D3); also elsewhere on the board
/Amp/Mux1SelC: A1.7 (D4); also elsewhere on the board
/Amp/Mux2SelA: A1.8 (D5); also elsewhere on the board
/Amp/Mux2SelB: A1.9 (D6); also elsewhere on the board
/Amp/Mux2SelC: A1.10 (D7); also elsewhere on the board
/Amp/Mux3SelA: A1.11 (D8); also elsewhere on the board
/Amp/Mux3SelB: A1.12 (D9); also elsewhere on the board
/Amp/Mux3SelC: A1.13 (D10); also elsewhere on the board
/LED_Data: A1.14 (MOSI), J2.2
/Out1: A1.19 (A0); also elsewhere on the board
/Out2: A1.20 (A1); also elsewhere on the board
/Out3: A1.21 (A2); also elsewhere on the board
GND: A1.4 (GND), A1.29 (GND), C7.2, C8.2, J1.4, J2.3, J3.13, J3.26, J4.2, U5.2 (GND); also elsewhere on the board
PD1: J3.1; also elsewhere on the board
PD2: J3.2; also elsewhere on the board
PD3: J3.3; also elsewhere on the board
PD4: J3.4; also elsewhere on the board
PD5: J3.5; also elsewhere on the board
PD6: J3.6; also elsewhere on the board
PD7: J3.7; also elsewhere on the board
PD8: J3.8; also elsewhere on the board
PD9: J3.9; also elsewhere on the board
PD10: J3.10; also elsewhere on the board
PD11: J3.11; also elsewhere on the board
PD12: J3.12; also elsewhere on the board
PD13: J3.14; also elsewhere on the board
PD14: J3.15; also elsewhere on the board
PD15: J3.16; also elsewhere on the board
PD16: J3.17; also elsewhere on the board
PD17: J3.18; also elsewhere on the board
PD18: J3.19; also elsewhere on the board
PD19: J3.20; also elsewhere on the board
PD20: J3.21; also elsewhere on the board
PD21: J3.22; also elsewhere on the board
PD22: J3.23; also elsewhere on the board
PD23: J3.24; also elsewhere on the board
PD24: J3.25; also elsewhere on the board

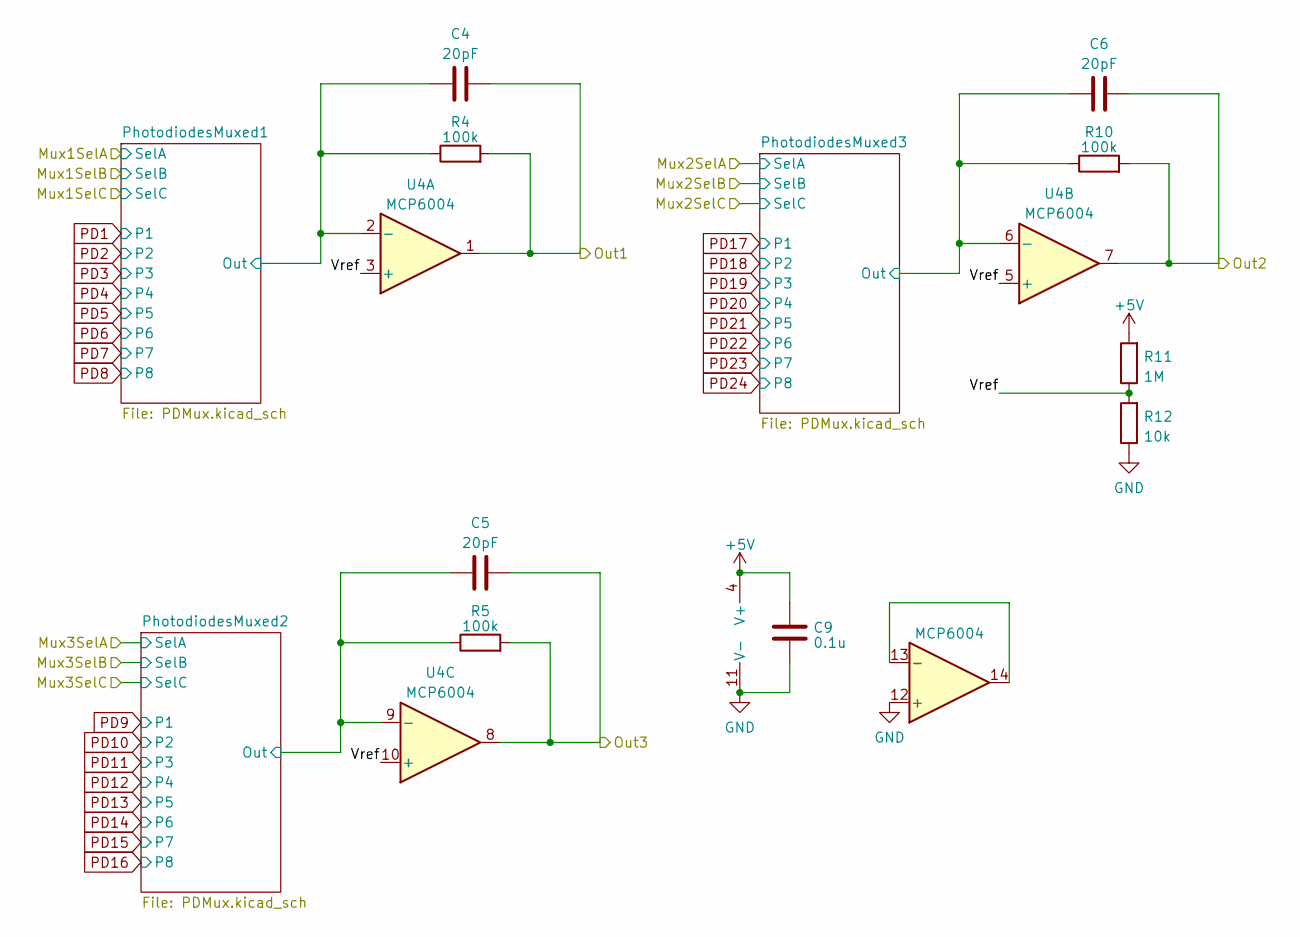
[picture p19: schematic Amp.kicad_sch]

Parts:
C4, C5, C6: 20pF; C_Disc_D5.1mm_W3.2mm_P5.00mm
C9: 0.1u; C_Disc_D5.1mm_W3.2mm_P5.00mm
R4, R5, R10: 100k; R_Axial_DIN0204_L3.6mm_D1.6mm_P5.08mm_Horizontal
R11: 1M; R_Axial_DIN0204_L3.6mm_D1.6mm_P5.08mm_Horizontal
R12: 10k; R_Axial_DIN0204_L3.6mm_D1.6mm_P5.08mm_Horizontal
U4: MCP6004; DIP-14_W7.62mm

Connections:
+5V: C9.1, R11.2, U4.4 (V+); also elsewhere on the board
/Amp/PhotodiodesMuxed1/Out: C4.1, R4.1, U4.2 (-); also elsewhere on the board
/Amp/PhotodiodesMuxed2/Out: C5.1, R5.1, U4.9 (-); also elsewhere on the board
/Amp/PhotodiodesMuxed3/Out: C6.1, R10.1, U4.6 (-); also elsewhere on the board
/Amp/Vref: R11.1, R12.2, U4.3 (+), U4.5 (+), U4.10 (+)
/Out1: C4.2, R4.2, U4.1; also elsewhere on the board
/Out2: C6.2, R10.2, U4.7; also elsewhere on the board
/Out3: C5.2, R5.2, U4.8; also elsewhere on the board
GND: C9.2, R12.1, U4.11 (V-), U4.12 (+); also elsewhere on the board
unnamed: U4.13 (-), U4.14

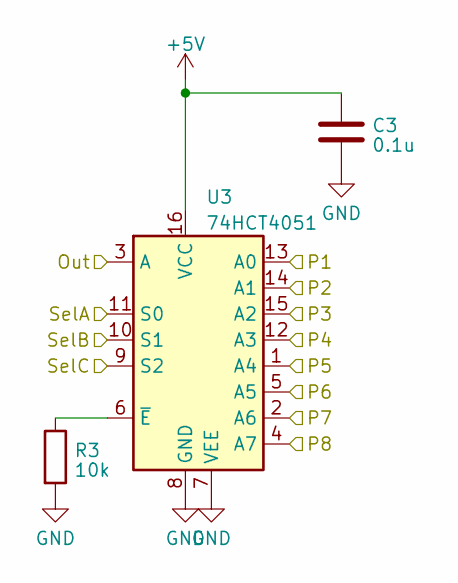
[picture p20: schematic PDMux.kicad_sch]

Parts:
C3: 0.1u; C_Disc_D5.1mm_W3.2mm_P5.00mm
R3: 10k; R_Axial_DIN0204_L3.6mm_D1.6mm_P5.08mm_Horizontal
U3: 74HCT4051; DIP-16_W7.62mm

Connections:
+5V: C3.1, U3.16 (VCC); also elsewhere on the board
/Amp/Mux1SelA: U3.11 (S0); also elsewhere on the board
/Amp/Mux1SelB: U3.10 (S1); also elsewhere on the board
/Amp/Mux1SelC: U3.9 (S2); also elsewhere on the board
/Amp/PhotodiodesMuxed1/Out: U3.3 (A); also elsewhere on the board
GND: C3.2, R3.2, U3.7 (VEE), U3.8 (GND); also elsewhere on the board
unnamed: R3.1, U3.6 (~E)
PD1: U3.13 (A0); also elsewhere on the board
PD2: U3.14 (A1); also elsewhere on the board
PD3: U3.15 (A2); also elsewhere on the board
PD4: U3.12 (A3); also elsewhere on the board
PD5: U3.1 (A4); also elsewhere on the board
PD6: U3.5 (A5); also elsewhere on the board
PD7: U3.2 (A6); also elsewhere on the board
PD8: U3.4 (A7); also elsewhere on the board

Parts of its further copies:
C1, C2: 0.1u; C_Disc_D5.1mm_W3.2mm_P5.00mm
R1, R2: 10k; R_Axial_DIN0204_L3.6mm_D1.6mm_P5.08mm_Horizontal
U1, U2: 74HCT4051; DIP-16_W7.62mm

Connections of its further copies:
+5V: C1.1, C2.1, U1.16 (VCC), U2.16 (VCC); also elsewhere on the board
/Amp/Mux2SelA: U2.11 (S0); also elsewhere on the board
/Amp/Mux2SelB: U2.10 (S1); also elsewhere on the board
/Amp/Mux2SelC: U2.9 (S2); also elsewhere on the board
/Amp/Mux3SelA: U1.11 (S0); also elsewhere on the board
/Amp/Mux3SelB: U1.10 (S1); also elsewhere on the board
/Amp/Mux3SelC: U1.9 (S2); also elsewhere on the board
/Amp/PhotodiodesMuxed2/Out: U1.3 (A); also elsewhere on the board
/Amp/PhotodiodesMuxed3/Out: U2.3 (A); also elsewhere on the board
GND: C1.2, C2.2, R1.2, R2.2, U1.7 (VEE), U1.8 (GND), U2.7 (VEE), U2.8 (GND); also elsewhere on the board
unnamed: R1.1, U1.6 (~E)
unnamed: R2.1, U2.6 (~E)
PD9: U1.13 (A0); also elsewhere on the board
PD10: U1.14 (A1); also elsewhere on the board
PD11: U1.15 (A2); also elsewhere on the board
PD12: U1.12 (A3); also elsewhere on the board
PD13: U1.1 (A4); also elsewhere on the board
PD14: U1.5 (A5); also elsewhere on the board
PD15: U1.2 (A6); also elsewhere on the board
PD16: U1.4 (A7); also elsewhere on the board
PD17: U2.13 (A0); also elsewhere on the board
PD18: U2.14 (A1); also elsewhere on the board
PD19: U2.15 (A2); also elsewhere on the board
PD20: U2.12 (A3); also elsewhere on the board
PD21: U2.1 (A4); also elsewhere on the board
PD22: U2.5 (A5); also elsewhere on the board
PD23: U2.2 (A6); also elsewhere on the board
PD24: U2.4 (A7); also elsewhere on the board

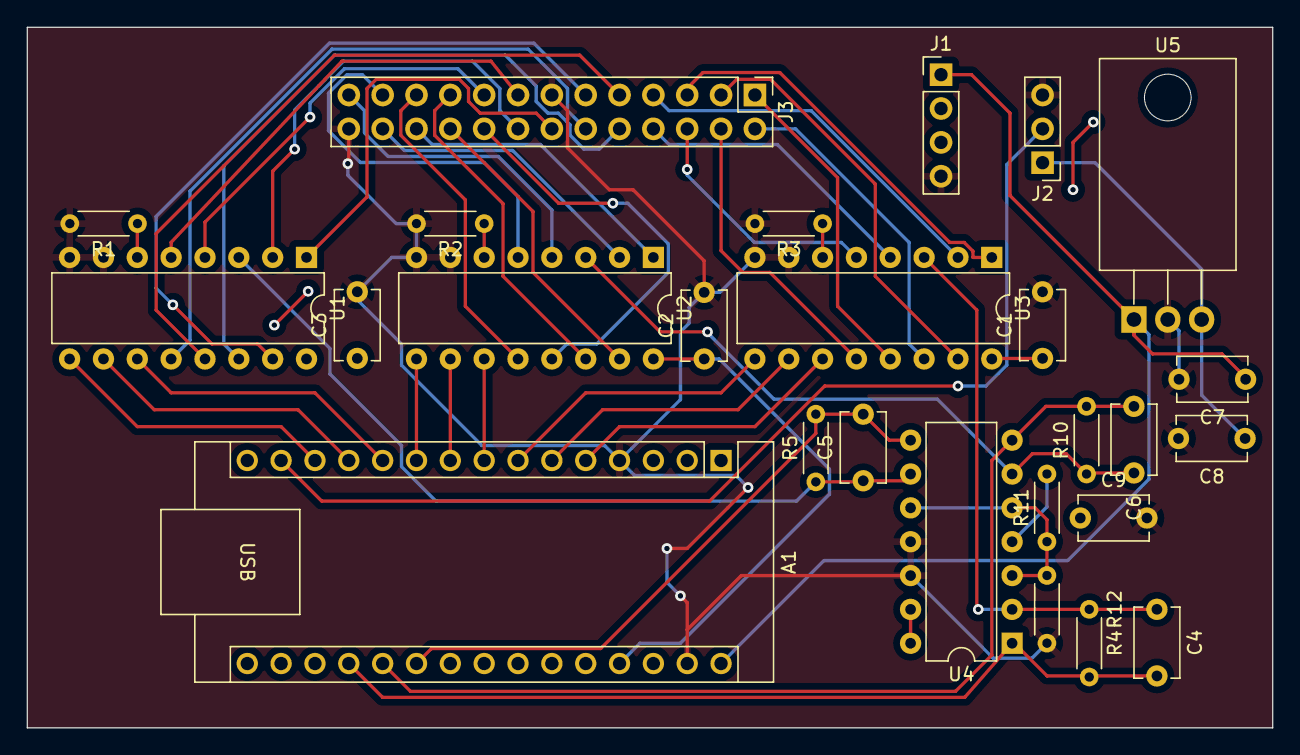
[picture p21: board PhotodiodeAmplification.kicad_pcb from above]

Board: 2 copper layers, 93.5 x 52.6 mm, 26 parts (0 on the bottom side), 49 nets.

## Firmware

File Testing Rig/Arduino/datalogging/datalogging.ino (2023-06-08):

#define NUMBER_OF_MUX 3
#define NUMBER_OF_CHANNELS 8

// Assign the Arduino pins connected to the multiplexer
int sPins[NUMBER_OF_MUX][3] = {{2, 3, 4}, {5, 6, 7}, {8, 9, 10}};
int zPin[NUMBER_OF_MUX] = {A0, A1, A2};

void setup() {
  Serial.begin(9600);
  while (!Serial) ;  // Wait for serial connection

  // Set the select pins as outputs
  for (int i = 0; i < NUMBER_OF_MUX; i++) {
    for (int j = 0; j < 3; j++) {
      pinMode(sPins[i][j], OUTPUT);
    }
    pinMode(zPin[i], INPUT);
  }
}

void loop() {
  // Wait for command from the computer to start data logging
  while (!Serial.available()) ;
  Serial.println("start");

  // Read the command from the computer
  char command = Serial.read();
  
  if (command == 's') {
    // Start data logging
    
    // Send acknowledgment to the computer
    Serial.println("start");
    
    // Log the data until receiving the stop command
    while (!Serial.available() || Serial.read() != 'e') {
      // Read and send the photodiode values
      for (int i = 0; i < NUMBER_OF_MUX; i++) {
        for (int j = 0; j < NUMBER_OF_CHANNELS; j++) {
          // Set the select pins for the current channel
          for (int k = 0; k < 3; k++) {
            digitalWrite(sPins[i][k], bitRead(j, k));
          }

          // Read the photodiode value
          int photodiodeValue = analogRead(zPin[i]);
          Serial.print(photodiodeValue);
          
          if(i == NUMBER_OF_MUX -1 && j == NUMBER_OF_CHANNELS -1){
          }else{
            Serial.print(",");
        }
      }
      Serial.println();
      // Delay before sending the next set of data
      delay(100);
    }
    
    // Send acknowledgment to the computer
    Serial.println("stop");
    
    // Wait for the computer to acknowledge the stop command
    while (!Serial.available()) ;
    while (Serial.read() != 'stop') ;
    
    // Log the completion message to the computer
    Serial.println("Data logging complete!");
 

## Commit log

2023-06-03 Initial commit - collating everything
    [ADCBank.kicad_sch, Amp.kicad_sch, PDADCModule.kicad_sch, PDMux.kicad_sch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]
2023-06-04 Changed dir structure
    [ADCBank.kicad_sch, Amp.kicad_sch, PDADCModule.kicad_sch, PDMux.kicad_sch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]
2023-06-04 Retried dir structure
    [ADCBank.kicad_sch, Amp.kicad_sch, PDADCModule.kicad_sch, PDMux.kicad_sch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]
2023-06-06 design files for lighting rig
    [hinge_tube_left.SLDPRT, hinge_tube_right.SLDPRT, prototype.SLDASM]
2023-06-06 design files for testing rig
    [base.SLDPRT, base.STL, sensor_collar.SLDPRT, sensor_collar.STL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]
2023-06-07 Update and rename README.md to Circuit Documentation.md
2023-06-07 Update Circuit Documentation.md
2023-06-08 Document circuit design and sims
